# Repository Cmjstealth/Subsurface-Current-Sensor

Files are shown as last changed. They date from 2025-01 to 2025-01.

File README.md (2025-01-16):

# Subsurface-Current-Sensor
Deployable low cost DIY sensor buoy for logging subsurface current speed, direction, water temperature, etc at common recreational diving depths (0-130ft). Note this project is still an incomplete and untested work in progress. Several components still need to be developed before an initial test.

The goal is to develop an automated sensor and data logger device that could be cheaply ($60?) built in with common components and 3d printable parts. A device that could be deployed via scuba for several months to collect automated time series data such as water current speeds, direction, temperature, salinity, etc. 

Similar to the open source CTD strategy of oceanographyforeveryone.com, this project aims to enable researchers and marine enthusiasts by reduce the financial barrier to collecting key data about our underwater world at scale. The initial design is focused on an negatively buoyant, entirely subsurface tilt sensor. This would allow it to be “hung” from existing structures (with owner permission) that are already permitted and avoid often length regulatory processes often faced by new deployments. In areas where no such structure exists a simple subsurface float could be attached to a temporary anchor.

Our pilot project is in the Salish sea of Washington state where there is an opportunity to model currents and temperatures at the highly-specific locations used for recreational scuba diving. This should allow the development of better current prediction guidelines for the local dive community. Site specific water quality data would also be valuable for modeling and better understanding trends observed in existing volunteer marine species monitoring projects at these same locations such as the Reef.org fish survey project, reefcheck.org kelp monitoring surveys, the YOY Rockfish survey, etc.

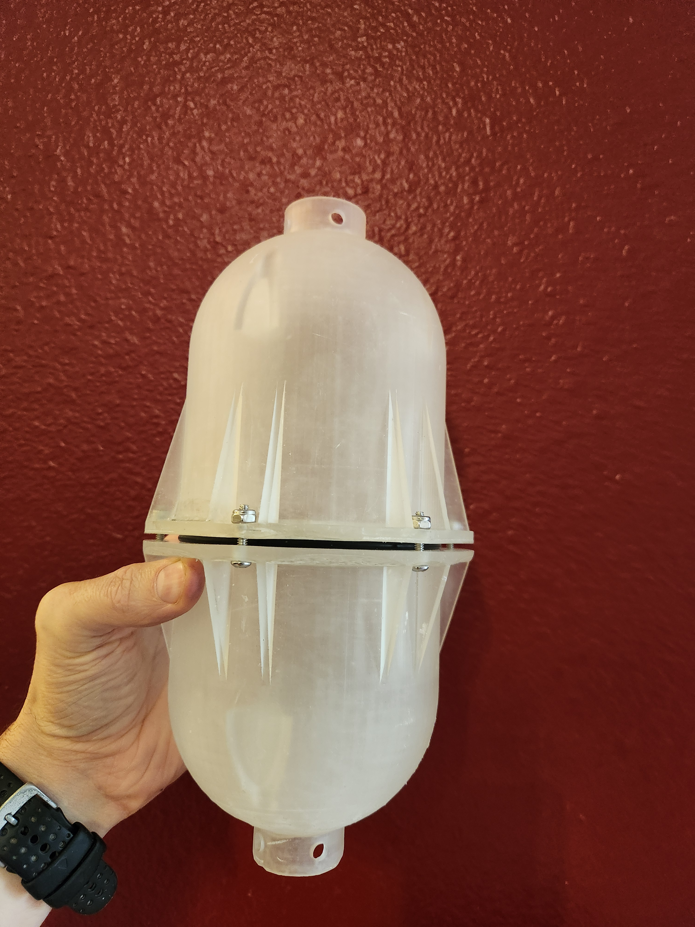
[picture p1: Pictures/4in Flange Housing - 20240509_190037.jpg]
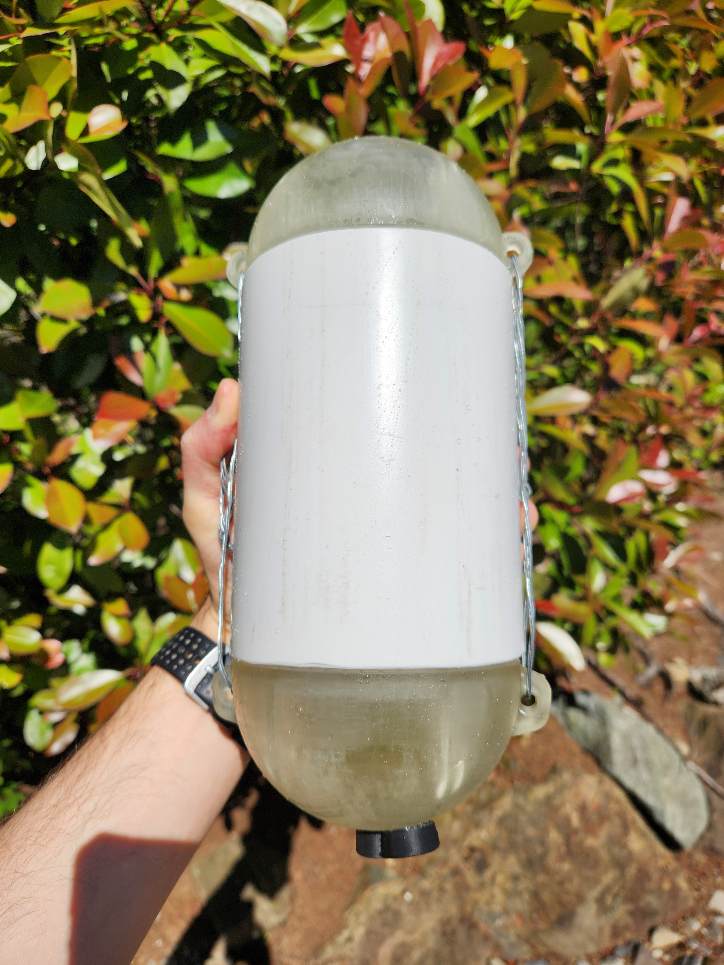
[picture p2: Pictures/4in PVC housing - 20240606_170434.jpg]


<u>Some project notes</u>:
- Initial version powered by 3 D batteries in series without any voltage regulator (3.6v-4.5v).
- Data is saved on an internal SD card that can be removed after sensor recovery
- Operated with a 2 position magnetic switch
  - On (continuous operation): Takes measurements every few seconds useful for collecting calibration data
  - Off (power save): the mode used when deployed for (hopefully) several months at a time
  - Remove at least one battery to complete turn off 

Water current speed calibration idea so far (untested):
  - Hang sensor from a surface float. Need gps with tracking turned on and the clock synchronized with the sensor's RTC. Line attached from surface float to a boat somewhere well clear of paddle or prop wash effects.
  - Boat can then tow the float at a slow continuous speed holding a known compass heading on a calm day for a minute or so. Repeat at perhaps 2 other speeds.
  - Then repeat all those same known speeds on a reciprocal compass heading to cancel out potential differences in speed through water vs speed over ground (due to current or wind).
  - This data could be used for a regression analysis so the sensor's raw tilt values can be used to predict current speed values.

This repository includes files for several variants of the housing design
  - **"4in PVC housing cap"** is what I'm currently testing. It uses 6" of standard 4" PVC purchased from home depot. This way only the end caps need to be 3d printed reducing resin cost, print time, and post-print finishing workload. A 4" Diameter was chosen as it is big enough to accommodate the cheapest rechargeable lead acid batteries. This could be desirable over alkaline D batteries in a future turbine style current sensor capable of energy harvesting and powering higher current sensors, microprocessors, or radio transceivers.
  - **"4in Flange Housing"** is included as I built one and successfully pressure tested it however it requires a significant amount of resin to print. The flange design that compresses the O ring doesn't seem as robust either. It also requires a lot of stainless steel hardware.
  - **(2" design coming soon)** Since V1 will likely just be powered by disposable D batteries it probably makes sense to modify the PVC and resin printed housing cap design with something closer to a 2" diameter. It would make all the materials substantially cheaper (resin, pvc pipe, and o-rings). it should also be substantially easier to slide smaller end caps into the pipe. The 4" version requires lots of silicon lube and force to put on.

Tentative Component list:
|Component|Price $USD|Notes|
|--------------------|----------|----------------------------------------------------------------------------------------------------|
|Microprocessor: ATMEGA328P DIP-28 (chip only)|2.16|Low power processor|
|DIP-28 wide pin socket|0.78|To ease assembly and so the processor can be removed from pcb for programming bootloader|
|Micro SD Storage module|0.73|Needed to save data to a sd card|
|Small 16GB Micro SD Card|2.2|Don't need much space but I've had trouble with generic brand cards.Microdrive brand availible on aliexpress|
|GY-273 HMC5883L Triple Axis Compass Magnetometer Sensor Module|2.16|To determine magnetic direction of tidal current|
|PCF8563T IIC Real Time Clock Module|1.11|microoprocessor doesn't have any persistant way of knowing the date/time to log with observations.|
|DS18B20 Digital Temperature Sensor|0.688|Accurate within 0.5 degree C. Low power. Pre-calibrated.|
|ADXL362 3-Axis Digital Accelerometer Sensor|2.87|for tilt sensor design|
|LM1117 3.3v voltage regulator|0.43|Draws 5mA when not in use so will need to be powered down when not in use|
|2N3904 and 2N3906 transistors|0.4|for switching on/off sensors, buzzers, etc|
|5v Buzzer|0.37|To give indication of sucessful power on|
|2x Magnetic reed switches|0.3||
|Single sided copper pcb board|1|Est cost each… would likely CNC multiple boards at once from a single large sheet|
|Other assorted electrical components (resistors, diodes, solder, etc)|2|Just a ballpark cost estimate for now|
|3x D Battery holders|2.91||
|PVC Pipe|5||
|4x O rings 100mm OD 4mm dia|2.72||
|Assorted stainless screws, stainless swivels, zip ties, mounting hardware,etc|5||
|3d printing liquid resin|9||
|3d printing filiment|3||
|Tax|3.2828||
|Total|48.1108||

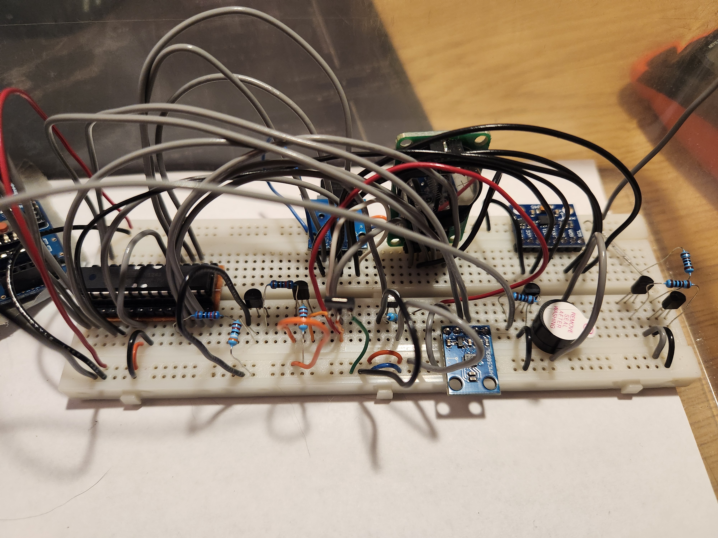
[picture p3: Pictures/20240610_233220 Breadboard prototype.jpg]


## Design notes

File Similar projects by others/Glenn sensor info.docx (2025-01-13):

Glenn E. Grant

https://www.facebook.com/sciencetech

https://nwdiveclub.com/viewtopic.php?p=278531#p278531

2016

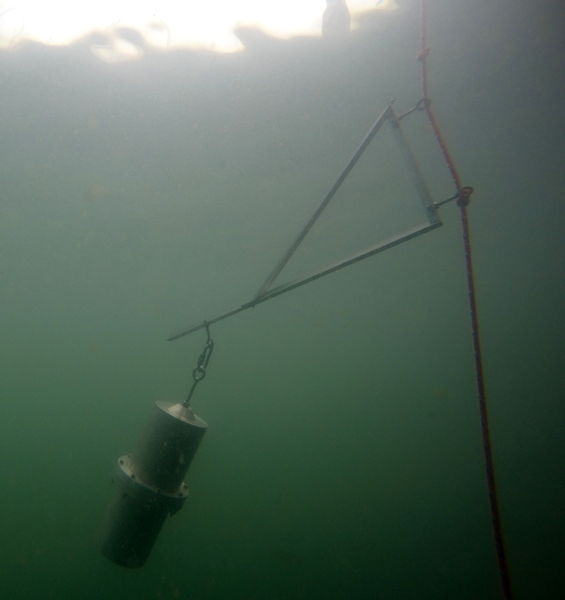
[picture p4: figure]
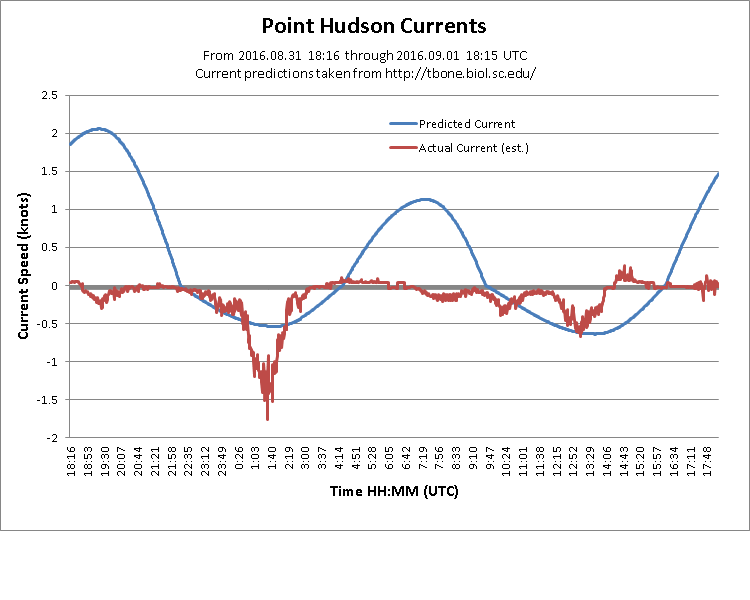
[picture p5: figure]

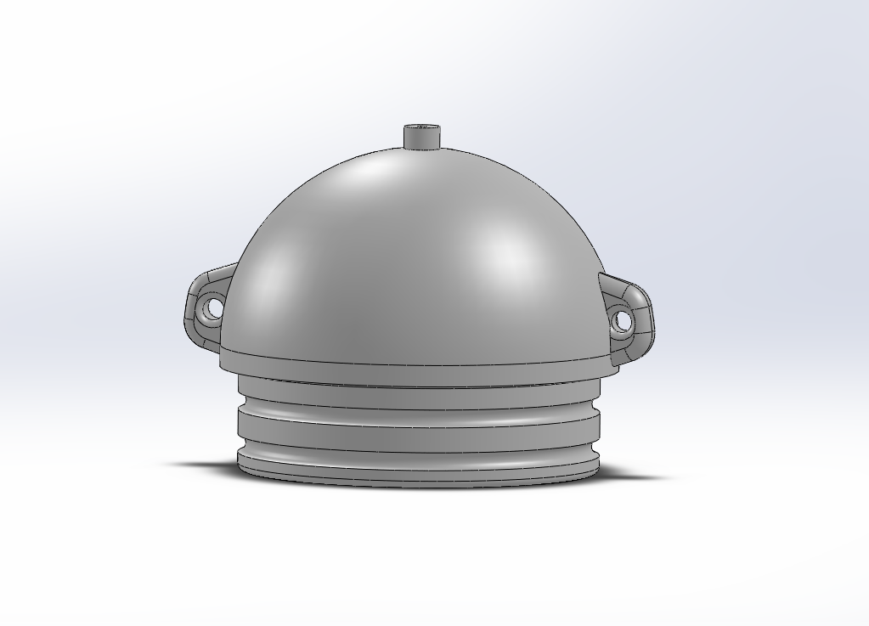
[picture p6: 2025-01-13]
Pictures/4in PVC housing cap v0.4 - CAD Design.png

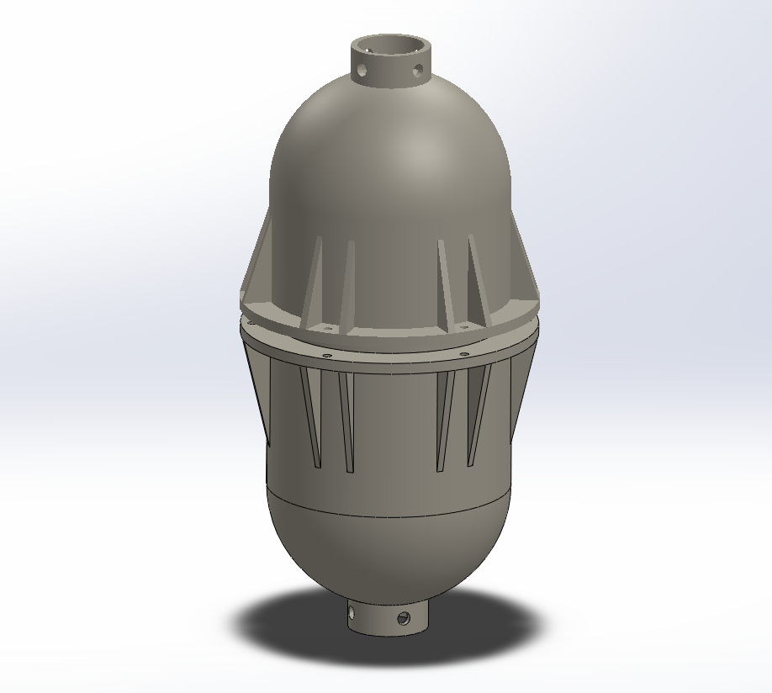
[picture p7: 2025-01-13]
Pictures/4in Flange Housing - CAD design.png

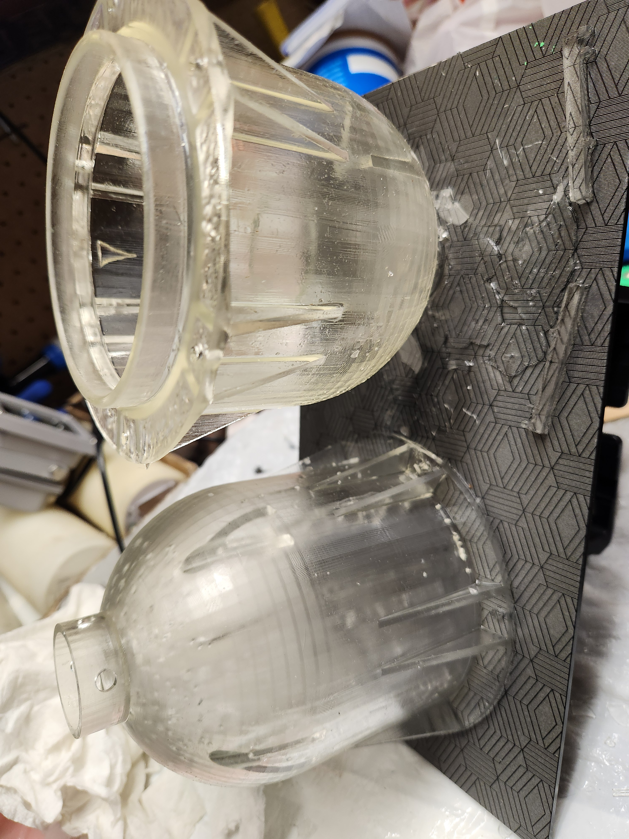
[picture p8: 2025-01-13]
Pictures/4in Flange Housing - 20240509_135228.jpg

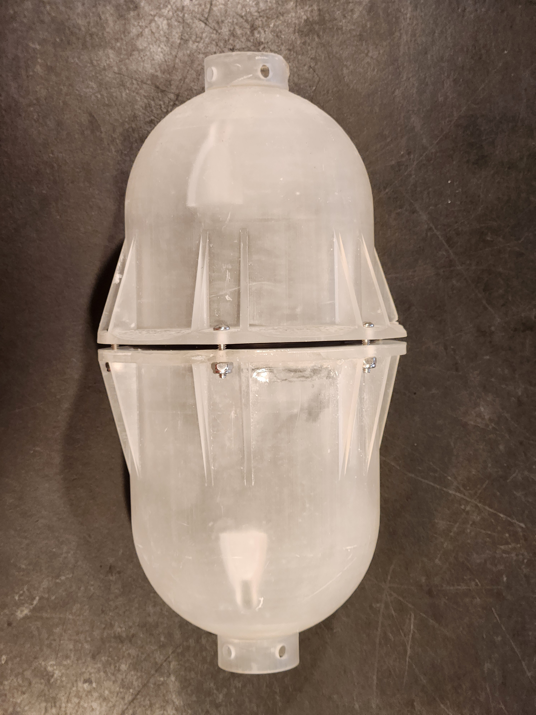
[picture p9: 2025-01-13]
Pictures/4in Flange Housing - 20240509_190154.jpg

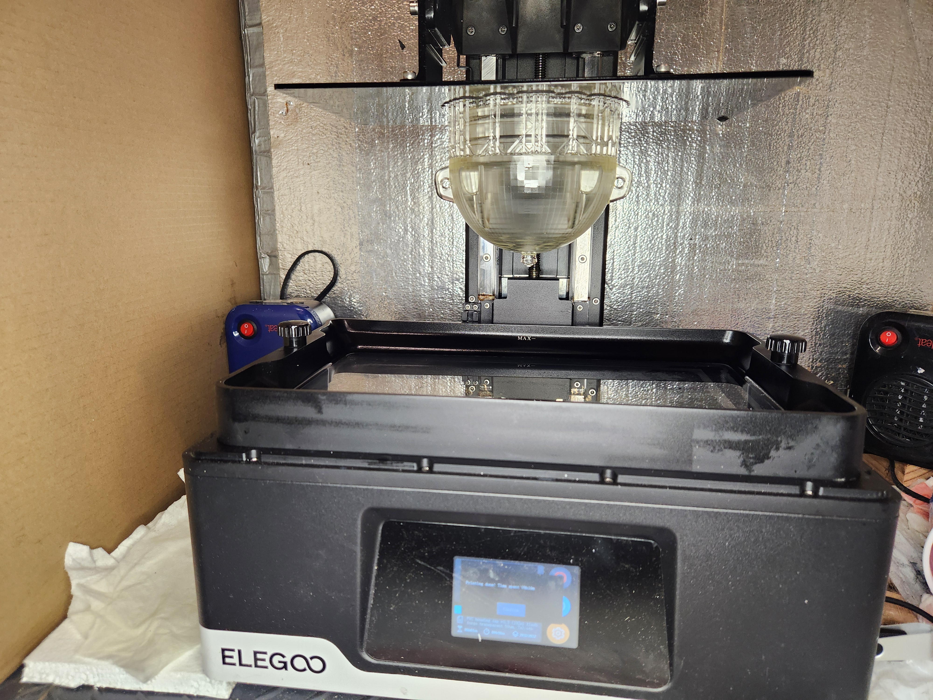
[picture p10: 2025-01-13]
Pictures/4in PVC housing - 20240605_170723.jpg

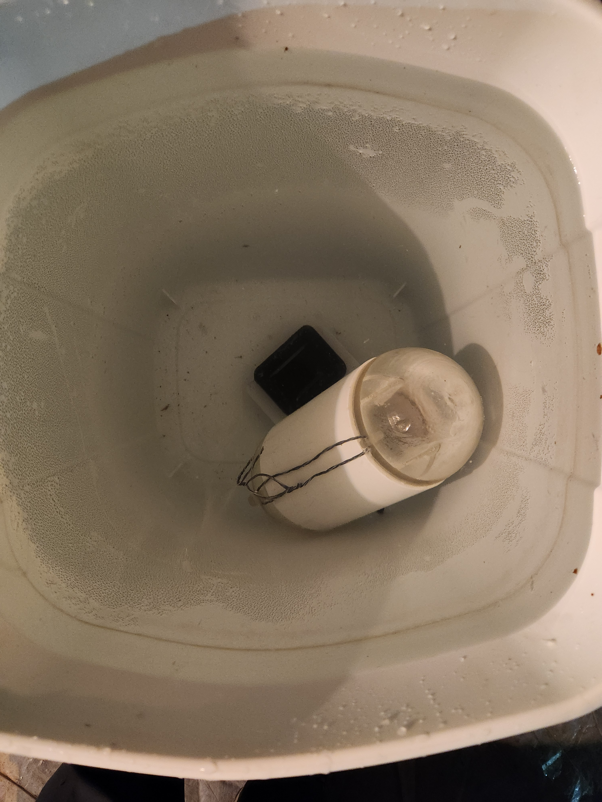
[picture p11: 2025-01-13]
Pictures/4in Flange Housing - 20240606_021940.jpg

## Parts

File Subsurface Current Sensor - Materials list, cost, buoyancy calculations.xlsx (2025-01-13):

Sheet: Materials
Component | Price | Notes | Example link
Microprocessor: ATMEGA328P DIP-28 (chip only) | $2.16 | Low power processor | https://www.aliexpress.com/item/3256806152938344.html
DIP-28 wide pin socket | $0.78 | To ease assembly and so the processor can be removed from pcb for programming bootloader
Micro SD Storage module | $0.73 | Needed to save data to a sd card | https://www.ebay.com/itm/285436222391
Small 16GB Micro SD Card | $2.20 | Don't need much space but I've had trouble with generic brand cards.Microdrive brand availible on aliexpress | https://www.ebay.com/itm/324736594273
GY-273 HMC5883L Triple Axis Compass Magnetometer Sensor Module | $2.16 | To determine magnetic direction of tidal current | https://www.ebay.com/itm/195942487206
PCF8563T IIC Real Time Clock Module | $1.11 | microoprocessor doesn't have any persistant way of knowing the date/time to log with observations. | https://www.ebay.com/itm/334893472046
DS18B20 Digital Temperature Sensor | $0.69 | Accurate within 0.5 degree C. Low power. Pre-calibrated. | https://www.ebay.com/itm/266531052031
ADXL362 3-Axis Digital Accelerometer Sensor | $2.87 | for tilt sensor design | https://www.ebay.com/itm/354987332435
LM1117 3.3v voltage regulator | $0.43 | Draws 5mA when not in use so will need to be powered down when not in use | https://www.aliexpress.us/item/2255800903886922.html
2N3904 and 2N3906 transistors | $0.40 | for switching on/off sensors, buzzers, etc
5v Buzzer | $0.37 | To give indication of sucessful power on | https://www.aliexpress.us/item/3256806022762450.html
2x Magnetic reed switches | $0.30 |  | https://www.aliexpress.us/item/3256805857131628.html
Single sided copper pcb board | $1.00 | Est cost each… would likely CNC multiple boards at once from a single large sheet | https://www.ebay.com/itm/166452012477
Other assorted electrical components (resistors, diodes, solder, etc) | $2.00 | Just a ballpark cost estimate for now
3x D Battery holders | $2.91 |  | https://www.aliexpress.com/item/3256806302793924.html
PVC Pipe | $5.00
4x O rings 100mm OD 4mm dia | $2.72 |  | https://www.aliexpress.com/item/3256806747371164.html
Assorted stainless screws, stainless swivels, zip ties, mounting hardware,etc | $5.00
3d printing liquid resin | $9.00
3d printing filiment | $3.00
Tax | $3.28
Total | $48.11
Components for alternate deisgns
MCP9808 high Accuracy I2C Temperature Sensor | $3.45 | ±0.25°C/0.0625°C | https://www.ebay.com/itm/276240809847 or https://www.aliexpress.us/item/3256805752894500.html
3x D Alkaline batteries | $4.89
DC-DC Buck Step-down Voltage regulator | $0.99 | Might need to experiment to find a voltage regulator that has a low power draw for standby operation | https://www.ebay.com/itm/113831704809
TS-300B Turbidity Sensor | $6.71 | Designed for washing machines but curious if it could be adapated to measure light attenuation in salt water | https://www.ebay.com/itm/315042911124
SIM800L GPRS GSM Phone Module | $5.44 | If mounted on a surface buoy would allow real time transmission of data and monitoring of hardware issues | https://www.ebay.com/itm/312693114822
GL5516 Photoresistor for ballpark light level estimation? | $0.05 | Would need anti-biofouling device. Not sure if useful proxy for photosynthetically active light levels?
Electrodes & simple circut for conductivity measurement (salinity estimation) | $4.00 | Untested idea. Unclear how quickly it would foul
TDS Sensor Water Conductivity Sensor for Arduino | $3.14 | 3.3~5.5V. Excitation source is an AC signal, effectively preventing probe polarization. Working current: 3~6mA | https://www.aliexpress.us/item/3256801512027885.html
Magnets and bearings for building a magnetically coupled shaft | ?
Ph Sensor | ? | Every cheap sensor I've tried falls out of calibration almost immediately
DIY Laser-induced floresence spectroscopy sensor? | ? | Maybe a fantasy, but cheap DIY approaches for this technique exist that could be done with higher power microprocessors and cheap camera sensors and uv diode lasers. Wonder if technique could be adapted to estimate chlorophyll or detect certain pollutants
Stainless electrode, transistor, and step up boost converter for measuring conductivity??? (salinity) | $4.00 | The microprocessor can easily measure voltage drop across known distance of water. Is this accurate enough to detect typical seawater salinity changes? Curious how long before the electrodes foul from ion buildup
Small DC motor for water flow sensing and battery charging | $3.00 |  | https://www.ebay.com/itm/324283294821
DC-DC boost converter (for charging SLA) | $3.80 | If charging from tidal current driven motor
UB645 6V 4aH Sealed lead acid rechargable battery | $9.62 | SLA batteries are crude but cheap and support continuous topping charges. (H) 3.98 x (L) 2.76 (W) 1.85 diag 3.32 | https://www.amazon.com/Replacement-Battery-Compatible-SLA0905-SLA090-4/dp/B0757MDCN2
O ring options
Nitrile Rubber O-Rings 100mm OD 92mm ID 4mm Width (5 pack) | $5.49
5 PCS Nitrile Rubber O-Rings Black 100mm OD 3.1mm Width | $4.84
Nitrile Rubber O-Rings 110mm OD 102mm ID 4mm Widthpack of 10 | $7.69

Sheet: Boyancy
Displacement | volume(cm^3)
PVC body - cyclinder 150mm tall and 114mm dia | 1531.05
End cap - sphere 111mm dia | 358.04
End cap - sphere 111mm dia | 358.04
Total | 1889.10
Mass fresh water g | 1889.098543
Mass salt water g | 1926.880513
Component | Mass in G
End cap | 209
End cap | 209
PVC body | 438
4 D Batteries | 544
PCB | 52
Internal structure carrige | 100
Concrete end cap weight 83mm dia half sphere with 20mm dia hole | 307.3
Concrete end cap weight 83mm dia half sphere with 20mm dia hole | 307.3
Total | 2166.520686
Additional trim weight needed (saltwater) | -239.640173

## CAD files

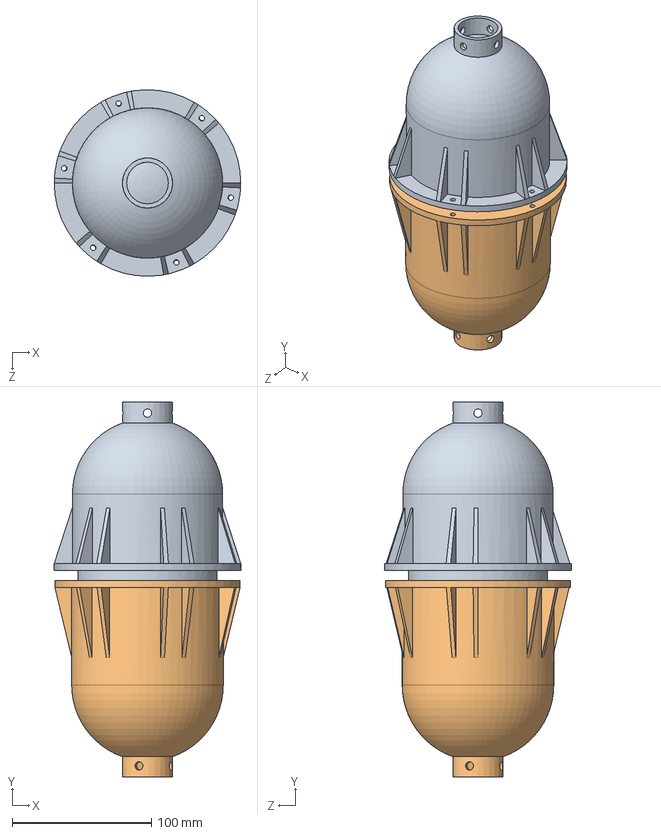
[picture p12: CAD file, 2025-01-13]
4in Flange Housing - Assembly.SLDASM
134.0 x 269.4 x 134.0 mm
4in Flange Housing - Top
4in Flange Housing - Bottom

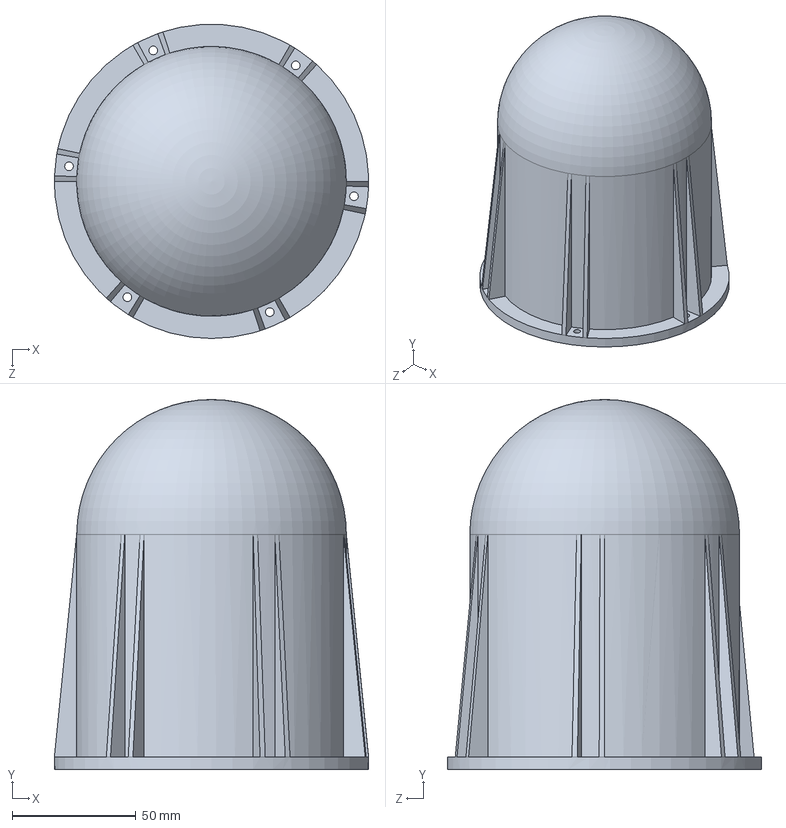
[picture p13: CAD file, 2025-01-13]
4in Flange Housing - Bottom.SLDPRT
127.0 x 149.5 x 126.9 mm

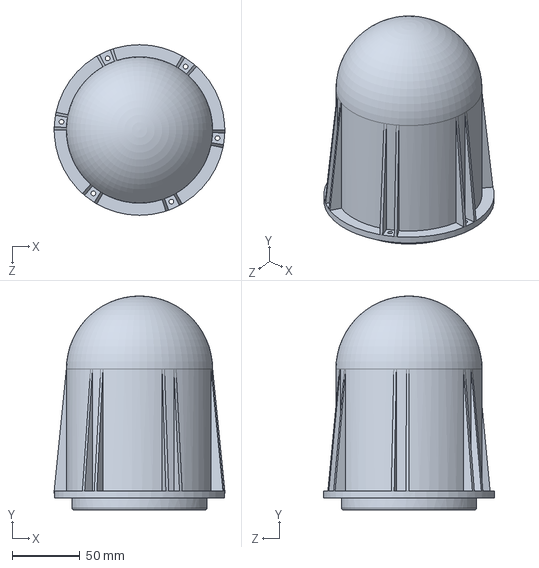
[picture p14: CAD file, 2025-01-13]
4in Flange Housing - Top.SLDPRT
126.0 x 158.0 x 126.0 mm

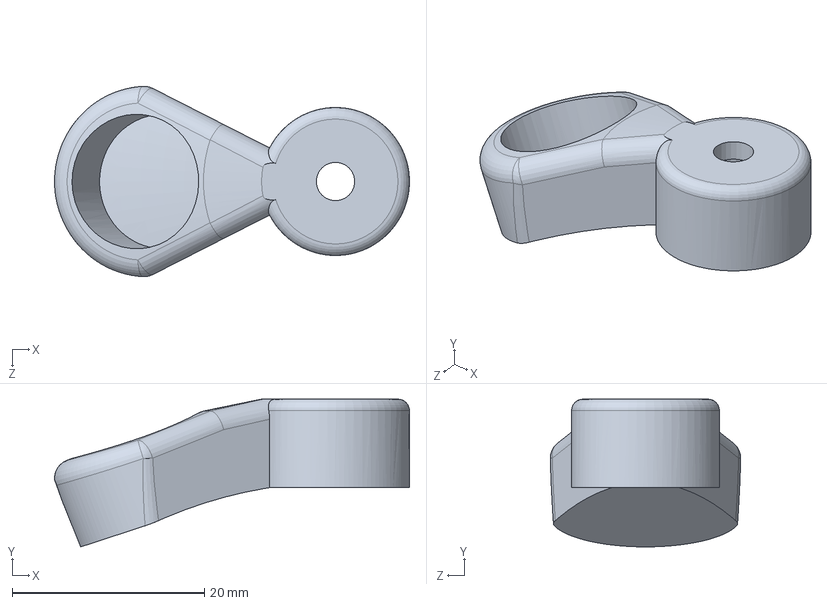
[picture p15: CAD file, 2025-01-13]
4in PVC housing cap Mode Selector Knob v0.2.SLDPRT
36.9 x 15.4 x 19.8 mm

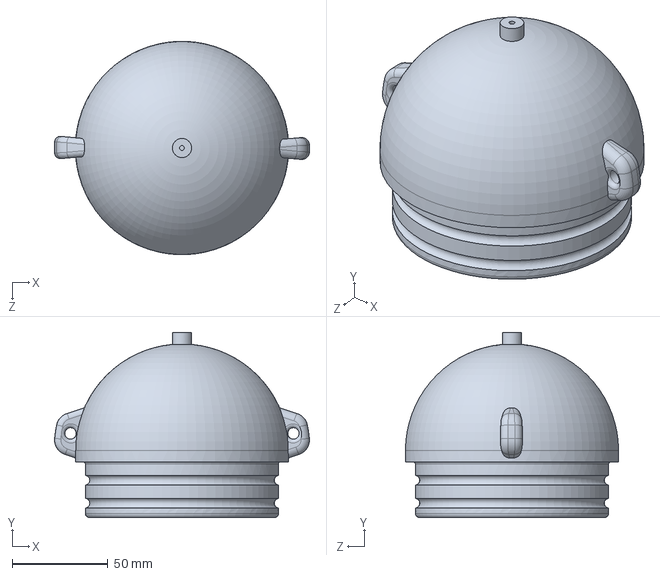
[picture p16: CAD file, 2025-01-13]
4in PVC housing cap v0.4.SLDPRT
133.4 x 96.8 x 111.5 mm

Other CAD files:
4in Flange Housing - Bottom.STL
4in Flange Housing - Top.STL
4in PVC housing cap Mode Selector Knob v0.2.STL
4in PVC housing cap v0.4.STL

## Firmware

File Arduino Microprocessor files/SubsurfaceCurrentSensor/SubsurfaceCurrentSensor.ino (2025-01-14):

#include <MemoryFree.h>
#include <Wire.h>
#include <math.h>

//pin assignments - NOTE: search the pin name to update the hard-coded pins in the code itself. This reduces vars and saves VERY limited microprocessor memory
// oneWirePin = 2;
// luxPin = A1;
// sensorPowerPin = 5;
// RTC_CLK_Pin = 6; RTC_DAT_Pin = 7; RTC_RST_Pin = 8;
// SPI_MOSI_Pin = 11; SPI_MISO_Pin = 12; SPI_CLK_Pin = 13;
// SD_CS_Pin = 4;
// ADXL345_CS = 3;
// I2C_SDA = A4; I2C_SCL = A5 // used for Compass

#include <virtuabotixRTC.h>
// Creation of the Real Time Clock Object. Example from https://miliohm.com/ds1302-rtc-with-arduino-tutorial/
virtuabotixRTC myRTC(6, 7, 8); // RTC_CLK_Pin = 6; RTC_DAT_Pin = 7; RTC_RST_Pin = 8;
String currentDateTimeString = "";
int newDateTimeArray[] = {0, 0, 0, 0, 1, 1, 2020}; //temp var to hold date an times in teh format of seconds, minutes, hours, day of the week, day of the month, month, year

//onewire temp stuff
#include <OneWire.h>
#include <DallasTemperature.h> //tip: if this library is too large try this instead: http://www.cupidcontrols.com/2014/10/moteino-arduino-and-1wire-optimize-your-read-for-speed/
#define ONE_WIRE_BUS 2 //oneWirePin D2
OneWire oneWire(ONE_WIRE_BUS); // Setup a oneWire instance to communicate with any OneWire devices
DallasTemperature sensors(&oneWire); // Pass our oneWire reference to Dallas Temperature

//SD Card stuff
#include <SPI.h>
#include <SD.h>
File myFile;

//ADXL345 stuff  // https://github.com/wollewald/ADXL345_WE/blob/main/examples/ADXL345_SPI_basic_data/ADXL345_SPI_basic_data.ino
#include <ADXL345_WE.h>
//#include <SPI.h>
#define CS_PIN 3  // ADXL345_CS = 3;
/* In case you want to change the default SPI pins (e.g. for ESP32), uncomment and adjust:
  #define MOSI_PIN 22
  #define MISO_PIN 17
  #define SCK_PIN 16
*/
bool spi = true;    // flag indicating that SPI shall be used
/* There are three ways to create your ADXL345 object in SPI mode:
 * ADXL345_WE myAcc = ADXL345_WE(CS_PIN, spi)     -> uses SPI, spi is just a flag, see SPI example
 * ADXL345_WE myAcc = ADXL345_WE(&SPI, CS_PIN, spi) -> uses SPI / passes the SPI object, spi is just a flag, see SPI example
 * ADXL345_WE myAcc = ADXL345_WE(&SPI, CS_PIN, spi, MOSI_PIN, MISO_PIN, SCK_PIN) -> like the latter, but also changes the SPI pins  
 */
ADXL345_WE myAcc = ADXL345_WE(CS_PIN, spi);
xyzFloat raw;
xyzFloat g;

// Digital compass stuff (HMC5883)
#include <MechaQMC5883.h>
MechaQMC5883 qmc;
int magX, magY, magZ, magAzimuth;

//other vars
unsigned long lastSerialDebugUpdateTime = 0; //for remembering the last time an update was sent to the serial port
unsigned long lastUpdateTime = 0; //for determining next time to pull data from sensors
//int avgLightInput = 0;
//int curLightInput = 0;
double currentTemp;
bool tempsRequested = false;
String receivedSerialData = "";

//temp vars
boolean tempBoolean;
char tempChar;
int tempInt;
double tempDouble;
String tempString;
unsigned long tempTime;

void setup() {
  Serial.begin(9600);
  Serial.println(F("SubsurfaceSensorBuoy 0.10"));

  pinMode(5, OUTPUT); //sensorPowerPin=5
  digitalWrite(5, HIGH); //sensorPowerPin=5
  delay(50); //wait for sensors to power on
  
  // Real time clock stuff
  //myRTC.setDS1302Time(0, 0, 0, 0, 1, 1, 2020); // Set the RTC's seconds, minutes, hours, day of the week, day of the month, month, year

  //onewire temp stuff
  sensors.begin(); // IC Default 9 bit. If you have troubles consider upping it 12. Ups the delay giving the IC more time to process the temperature measurement
  sensors.requestTemperatures(); // // Start calculating temperatures to use in next update

  // Digital compass stuff
  Wire.begin(); //for all I2c stuff
  qmc.init();
  
  // SD Card Reader Stuff
  if (!SD.begin(4)) { //SD_CS_Pin = 4;
    Serial.println(F("SD init fail"));
    //while (1);
  }else{
    Serial.println("SD init ok");
  }
  
  //ADXL345 stuff
  if(!myAcc.init()){
    Serial.println("ADXL345 not connected!");
  }
  //myAcc.setSPIClockSpeed(4000000); // You can set the SPI clock speed. Default is 5 MHz
  myAcc.setDataRate(ADXL345_DATA_RATE_12_5); //set data rate to 12.5hz
  myAcc.setRange(ADXL345_RANGE_4G); //Choose the measurement range 16g,8g,4g,2g
  // myAcc.setLowPower(true); //Uncomment to enable Low Power Mode. It saves power but slightly increases noise. LowPower only affetcs Data Rates 12.5 Hz to 400 Hz.

  //pinMode(5, OUTPUT); //sensorPowerPin=5
  //digitalWrite(5, LOW); //sensorPowerPin=5
}


void loop() {

  if (millis() > lastUpdateTime + 1000 && tempsRequested != true) {
    sensors.requestTemperaturesByIndex(0); // Start calculating temperatures now so they are ready by next update
    tempsRequested = true;
  }
  if (millis() > lastUpdateTime + 2000) { //get latest sensor values

    
    
    
    //get latest time
    myRTC.updateTime();
    currentDateTimeString = addLeadingZeroToInt(myRTC.year) + "-" + addLeadingZeroToInt(myRTC.month) + "-" + addLeadingZeroToInt(myRTC.dayofmonth) + " " + addLeadingZeroToInt(myRTC.hours) + ":" + addLeadingZeroToInt(myRTC.minutes) + ":" + addLeadingZeroToInt(myRTC.seconds);
    //Serial.println("Current Date / Time: " + currentDateTimeString);

    currentTemp = (double)sensors.getTempCByIndex(0);
    tempsRequested = false;

    qmc.read(&magX, &magY, &magZ,&magAzimuth); //get compass data

    //get ADXL345 values
    raw = myAcc.getRawValues();
    g = myAcc.getGValues();

    writeToFile(F("output.csv"), currentDateTimeString + "," + currentTemp + "," + magX + "," + magY + "," + magZ + "," + magAzimuth + "," + g.x + "," + g.y + "," + g.z);


    //dataArray[5] = analogRead(1); //dataArray[5]=luxRaw  //luxPin=A1
    //dataArray[6] = (double)(1.5915) * pow(2.7183, (0.0082)*dataArray[5]); //dataArray[6]=lux  //dataArray[5]=luxRaw

    ProcessSerialData();
    updateSerialDebug();
    lastUpdateTime = millis();
  }

  //restart device every 24hrs
  if (millis() >= 86400000) { //86400000 represents 24hrs in ms
    softReset(); //performs a soft reset (note: this method doesn't reset pin states or registers)
  }

} //end of void loop()






void updateSerialDebug() {
  if (millis() >= lastSerialDebugUpdateTime + 2000) {
    Serial.print(F("<freemem:")); Serial.print(freeMemory());
    Serial.print(F("; currentDateTimeString:")); Serial.print(currentDateTimeString);
    Serial.print(F("; currentTemp:")); Serial.print(currentTemp);
    Serial.print(F("; magX:")); Serial.print(magX);
    Serial.print(F("; magY:")); Serial.print(magY);
    Serial.print(F("; magZ:")); Serial.print(magZ);
    Serial.print(F("; magAzimuth:")); Serial.print(magAzimuth);
    Serial.print(F("; raw.x:")); Serial.print(raw.x);
    Serial.print(F("; raw.y:")); Serial.print(raw.y);
    Serial.print(F("; raw.z:")); Serial.print(raw.z);
    Serial.print(F("; g.x:")); Serial.print(g.x);
    Serial.print(F("; g.y:")); Serial.print(g.y);
    Serial.print(F("; g.z:")); Serial.print(g.z);
    //Serial.print(F("; luxRaw:")); Serial.print(dataArray[5]); //dataArray[5]=luxRaw
    Serial.println(F(">"));
    lastSerialDebugUpdateTime = millis();
  }
}


// Get commands received via serial port
void ProcessSerialData() {
  while (Serial.available() > 0) {
    tempChar = Serial.read();
    receivedSerialData += tempChar;
    if (tempChar == '\n') { //means we have received a complete line - time to process...

      if (receivedSerialData.indexOf("|setDT|") > -1) { //example input: "|setDT|0|10|5|6|26|4|2024" this command saves a new date and time using the folowing params: seconds, minutes, hours, day of the week, day of the month, month, year
        newDateTimeArray[0] = getDelimValue(receivedSerialData, '|', 2).toInt(); //seconds
        newDateTimeArray[1] = getDelimValue(receivedSerialData, '|', 3).toInt(); //min
        newDateTimeArray[2] = getDelimValue(receivedSerialData, '|', 4).toInt(); //hrs
        newDateTimeArray[3] = getDelimValue(receivedSerialData, '|', 5).toInt(); //day of week
        newDateTimeArray[4] = getDelimValue(receivedSerialData, '|', 6).toInt(); //day of month
        newDateTimeArray[5] = getDelimValue(receivedSerialData, '|', 7).toInt(); //month
        newDateTimeArray[6] = getDelimValue(receivedSerialData, '|', 8).toInt(); //year
        if (newDateTimeArray[6] != 0) { //for error checking lets just spot check that the last parameter exists and has the right number of digits
          myRTC.setDS1302Time(newDateTimeArray[0], newDateTimeArray[1], newDateTimeArray[2], newDateTimeArray[3], newDateTimeArray[4], newDateTimeArray[5], newDateTimeArray[6]); // Set the RTC's seconds, minutes, hours, day of the week, day of the month, month, year
          Serial.println(F("New DT set"));
        } else {
          Serial.println(F("Format Error"));
        }

      }

      receivedSerialData = "";
    } //end of if (tempChar == '\n')

    if (receivedSerialData.length() > 40) { //Received way more data than expected. lets clear receivedSerialData to avoid memory issues
      Serial.println(F("Excess input, purging"));
      receivedSerialData = "";
    }
  } //end of while (Serial.available()>0)
} //end of ProcessSerialData function





void writeToFile(String fileName, String dataToWrite) {
  // open the file. note that only one file can be open at a time,
  // so you have to close this one before opening another.
  myFile = SD.open(fileName, FILE_WRITE);
  // if the file opened okay, write to it:
  if (myFile) {
    myFile.println(dataToWrite);
    // close the file:
    myFile.close();
    //Serial.println(fileName + F(" written"));
  } else {
    // if the file didn't open, print an error:
    Serial.println(fileName + F(" error"));
  }
}


String addLeadingZeroToInt(int inputInt) {
  if (inputInt < 10) {
    tempString = "0" + (String)inputInt;
  } else {
    tempString = (String)inputInt;
  }
  return tempString;
}


String getDelimValue(String inputString, char delimChar, int valuePosition) {
  String requestedValue = "";
  int currentPosition = 0;
  char tempChar;
  for (int i = 0; i <= inputString.length(); i++) {
    tempChar = inputString.charAt(i);
    if (tempChar == delimChar) currentPosition++;
    if (tempChar != delimChar && currentPosition == valuePosition) requestedValue = requestedValue + (String)inputString.charAt(i);
  }//end of for
  return requestedValue;
} // end of getDelimValue function





void softReset() { //performs a soft reset (note: this method doesn't reset pin states or registers)
  asm volatile ("  jmp 0");
}

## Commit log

2025-01-13 Rename 20240610_233220 Breadboard prototype.jpg to Pictures/20240610_233220 Breadboard prototype.jpg
2025-01-13 Update and rename SubsurfaceCurrentSensor.ino to Arduino Microprocessor files/SubsurfaceCurrentSensor/SubsurfaceCurrentSensor.ino
